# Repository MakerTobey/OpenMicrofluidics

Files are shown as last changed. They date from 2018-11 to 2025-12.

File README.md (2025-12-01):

# Note: This repository is no longer expanded, instead, several concrete development projects have come out of it, including
* [A modular strobe workstation for microfluidic droplet generation](https://wenzel-lab.github.io/strobe-enhanced-microscopy-stage/)
* [A modular microfluidics flow controller](https://github.com/wenzel-lab/modular-microfluidics-workstation-controller)
* [RITMOS: Real-tIme Technology for Microfluidic drOplet Sorting](https://github.com/wenzel-lab/droplet-sorter-master/blob/main/README.md)
* [Syringe pumps optimised for microfluidics](https://github.com/wenzel-lab/syringe-pumps-and-controller)
* and more
* PLEASE SEE THE [REPOSITORIES OF OUR RESEARCH LABORATORY](https://github.com/orgs/wenzel-lab/repositories)

# Free and Open Source Microfluidics Research Hardware

This GitHub repository is an in-progress collection of Open Source Hardware instrumentation for microfluidics and ultra-high troughput lifescience experimentation research. This is a community driven effort and **you are invited to contribute thoughts, content, comments and help testing the instrumentation**! 

This projekt started as part of my Fellowship Freies Wissen (translates to Open Knowledge)2018-2019, here is the [project description on the corresponding Wikiversity page](https://de.wikiversity.org/wiki/Wikiversity:Fellow-Programm_Freies_Wissen/Einreichungen/Open_labware_for_better_life_science). And is beeing further developed as part of my reseach efforts as well as in my free time, togehter with various project partners, such advice and help from Daniel Mietchen, Patrick Hasenfeld, Nicolas Peschke, Biotop Community Heidelberg, the EMBL Workshops (especially Christian Arnold and Alejandro Gil Ortiz), and others.

## The following aim is addressed in this repository:

This is a list of microfluidics relevant Open Source Harwdare instrumentation, connected to the practical aim of testing the documentations by reading them carefully, by building the instrumentation in some cases (remotely and Heidelberg based workshop in early 2019) and further by testing, comparing and calibrating the equipement. **Everyone is welcome to contribute**.  Please contact me directly (Tobias.Wenzel /at/ embl.de) if you need financial help with hardware parts in oder to test the documentations and redocument them on [DocuBricks](docurbricks.com) to create more accessible, open hardware standard documentations.

### Happy contributing!

# Openess of microfluidics research & developement and ways forward

Increasing openess can be acheived in many different ways, such as increased accessibility of techniques or results to a professional or general audience, greater ease of use, increased mobility of researchers of different seniority, discipines or ethnicity into the field.
One aspect that enjoys recent popularity in microfluidic and bioprocess technologies is the "biohacker"or Do-It-Yourself (DIY) biology movement. The later includes self-made and low-cost research instrumentation.
Such advances in openess greatly improve the accessibility of microfluidic and related technology to lay people and have been reviewed recently [akerspaces." Trends in Biotechnology (February 3, 2017). https://doi.org/10.1016/j.tibtech.2017.01.001].
The open source hardware originating from this context does usually not, however, fulfill key application relevant criteria such as basic safety mechanisms (e.g. dremel fuge), bencharking calibration assessment (e.g. XXX), and documentation best practices as reccomended by the GOSH community [e.g. https://www.docubricks.com/best-practise-guide.jsp] or the Journal of Open Hardware, OSWA, etc.
For the above reasond of focus and qality management, here we focus on hardware and manufacturing related aspects of microfluidic and related technology for professional (in particular academic) applications.
In particular we probe 

(I) the use of open platforms and software.

(II) digitalisation and use/challenges of digital manufacturing

(III) identification of potentially valualble resources for microfluidic research drawing on digital manufacturing, open source and publis resources.
* high quality small-scale fluidic chip manufacturing techniques
* imaging of droplets (normal, fhigh-speed (e.g. stroboscopic+software), fluorescence)
* sorting of droplets (hardware-fast-processing, software, instructions)
* pressure control
* simlation tools
* open reagents 

# Free and Open Source Hardware resources of interest for testing and further development - selected promising resources

Any contribution and participation welcome! I am happy to connect and perhaps even help with resources, parts and potential parts-funding! Comment here, via issues, or email me.

## Open Dropseq station and Open Digital PCR

After looking at the details of the project, this seems like a fantastic piece of hardware and documentation. We will definitely try to build it and have already ordered all parts. Nice small and low-cost solutions for pressure controll. Parts are being purchased at the moment. Please look into the respective sub-repository: 

https://github.com/MakerTobey/OpenMicrofluidics/tree/master/Minidrop%20build%20and%20test

https://metafluidics.org/devices/minidrops/
https://www.nature.com/articles/s41467-017-02659-x#Sec9

### Open Fluorescence Activated Droplet Sorting

This is an active contsturction project! For files and progress, please look into the respective folder in this repository: https://github.com/MakerTobey/OpenMicrofluidics/tree/master/Open%20Fluorescence%20Activated%20Droplet%20Sorting%20(FADS)

FACS (Fluorescence Activated Cell Sorting) equivalent sorting of droplets for directed evolution and many other essays is a key method in microfluidics that only few labs master. One of the reasons is that few instructions are available (but they do exsist! See Christoph Merten in Nature Methods), and equipemnt is complex, propriatory and very expensive. A common work station for droplet sorting usually costs ca. 100.000 Euro. Now, an open source version (no propriatory sorware and harware lock-in, modifiable, modular and extensible) comes within reach!

## Open microfluidics pressure control

### Open syringepump(s)

http://www.appropedia.org/Open-source_syringe_pump
We have built two, but will further upgrade and test.

http://www.appropedia.org/Lynch_open_source_syringe_pump_modifications
https://www.sciencedirect.com/science/article/pii/S2468067218300269

We are building and testing some of this hardware! Please look into the respective project subfolder: https://github.com/MakerTobey/OpenMicrofluidics/tree/master/pressure%20control%20build%20and%20test

### Open pressure controll

My own project to build an ardunino based 2-channel pressure controll (pressure derived from a compressor), to be extended and tested: https://www.docubricks.com/viewer.jsp?id=6067044959053384704 Also explore our seperate GitHub repository: https://github.com/MakerTobey/uFluid

This project looks similar and deserves further attention: https://hackaday.io/project/148274-electronic-pressure-regulator, https://github.com/watsaig/ufcs-pc

A useful manifold for quake-style valves, already build and soon to be tested: https://github.com/GNHua/valve-control

Another useful manifold for quake-style valves, to be tested soon: https://metafluidics.org/devices/32-channel-controller/ Is this documentation incomplete?

In this project and with colleagues, we are following up on thiese hardware pieces. The Minidrop station includes another curstom pressure controll implementation.

## Open digital microfluidics ... and other related

OpenDrop
http://www.gaudi.ch/GaudiLabs/?page_id=392

And Dropbot
http://microfluidics.utoronto.ca/dropbot/

## Open digital microscopy

Open Flexure Microscope
https://aip.scitation.org/doi/10.1063/1.4941068
https://www.docubricks.com/viewer.jsp?id=6067044959053384704
with objective:
https://github.com/rwb27/openflexure_microscope
with motorisation:
https://github.com/rwb27/openflexure_nano_motor_controller
We are currently waiting for the new release (large, with automation and objective) to build one.

FlyPi:
https://open-labware.net/projects/flypi/
https://journals.plos.org/plosbiology/article?id=10.1371/journal.pbio.2002702

## Open fast-imaging solutions

Note: in the meanwhile, a sulution has been published: https://www.hardware-x.com/article/S2468-0672(22)00112-2/fulltext. We have also implemented and tested our own modular-but-integrated solution which can be found in our open microfluidics workstation repository: https://github.com/wenzel-lab/open-microfluidics-workstation

No microfluidics related fast imaging open hardware projects are konwn to us so far! Please let me know if you are aware of a resource. Fast-responding cameras would be great or stroboscopic illumination for droplet microfluidics.

I believe that stroboscopic imaging has already been build by many labs. Who would be interested to publish the designs openly?

Paper references of possible interest:
https://www.hindawi.com/journals/jamc/2009/198732/
https://aapt.scitation.org/doi/abs/10.1119/1.4863916
https://www.mdpi.com/2072-666X/8/12/351
https://www.future-science.com/doi/abs/10.2144/000112220
https://www.sciencedirect.com/science/article/pii/S0165027012003846
This link is broken at the moment! What content was here?  -> https://media.proquest.com/media/pq/classic/doc/4322030507/fmt/ai/rep/NPDF?_s=EUAbzVz%2B%2FEKGyiix9oguFSmtgAU%3D

Maybe:
https://pdfs.semanticscholar.org/63f0/b73d48380f3d5d3614e0fe12ae55adaeb1dd.pdf
https://www.spiedigitallibrary.org/conference-proceedings-of-spie/5145/0000/Simultaneous-mapping-of-phase-and-amplitude-of-MEMS-vibrations-by/10.1117/12.500138.short?SSO=1
https://scholar.google.de/scholar?hl=en&as_sdt=0%2C5&as_vis=1&q=stroboscopic%2Billumination%2Bmicroscope%2Barduino&btnG=
https://journals.plos.org/plosone/article?id=10.1371/journal.pone.0143547
https://pubs.acs.org/doi/abs/10.1021/ja074704l

Open Source imaging chips:
https://wiki.apertus.org/index.php/Main_Page

Open Source imaging software:
https://www.osapublishing.org/boe/abstract.cfm?uri=boe-1-2-385

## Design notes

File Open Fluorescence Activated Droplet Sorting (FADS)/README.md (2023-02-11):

# Open Fluorescence Activated Droplet Sorting (Open FADS)

FACS (Fluorescence Activated Cell Sorting) equivalent sorting of droplets for directed evolution and many other essays is a key method in microfluidics that only few labs master. One of the reasons is that few instructions are available (but they do exsist! See Christoph Merten in Nature Methods), and equipemnt is complex, propriatory and very expensive. A common work station for droplet sorting usually costs ca. 100.000 Euro. Now, an open source version (no propriatory sorware and harware lock-in, modifiable, modular and extensible) comes within reach! 

The current focus of this project is the FPGA data processing, which is worked on in this repository: https://github.com/MakerTobey/Open_FADS_FPGA_control
We are now also finalising the optomechanics part of the project here: [https://github.com/WenzelLab/Open_FADS_optomechanics](https://github.com/wenzel-lab/Open_FADS_optomechanics)

# These are the things needed for a FADS workstation:

## light source
This requires a strong lightsource (laser, most commonly 488nm {for Green Fluorescent Protein (GFP), red RFP and similar}, collimated, small elliptical focal spot, low coherence to avoid speckles) to activate fluorescence. Lasers usually cost several thousand Euro but some cheaper ones are available at slightly different wavelengths https://www.dragonlasers.com/blue-laser-pointers.html. Usually one has to calculate with a few thousand Euro per laser and some additional hundred Euro for the optics (not counting a professional microscope). Here we explore how to keep costs reasonably low while maintaining the quality and specifications of the setup.

## fast and sensitive fluorescence detection
It requires a fast and very sensitive detector for the fluorescent signal. This is commonly a PMT (photomultiplier tube), but now there are cheaper and less-easy-to-break APDs (avalanche photodiode)s. Individually they should cost in the order of magnitude of a hundred Euro, but they need to be hosted on a controller, cooling, etc. unit with appropriate connector, which usually spikes the cost to thousands. However, now there is work on an open source APD controller:
OpenAPD:

http://www.gaudi.ch/GaudiLabs/?page_id=718

Some circuits (e.g. amplification) might be useful from the CosmicPi projekt:

https://github.com/CosmicPi/CosmicPiV1.6PCB

https://ieeexplore.ieee.org/document/5158737

Here we use a non-open source, but lower noise, more modern, silicon based (does not break as easily) SiPM module from Ketek in Germany.

## fast data processing
And then there is a need for a very fast real-time logical processor chip, which is usually achieved by programming an FPGA chip. This chip will read the signal and make a decision whether or not to activate the droplet sorter. (For example: Positive signal is coming in, intensity and duration (width) is in the right range and there was no other signal too shortly before, so OK, activate the amplifier trigger for the sorting electrode.) FPGAs are usually not exacly user friendly as they are programmed in a bottom-level hardware language. Easy-to-use systems (with integrated top level languages for programming and common measurement-tech interfaces) usually some in a propriatory environment and are very expensive. However, there has been a lot of activity in the respective open source landscape recently.

Medium cost, established for science measurements:

Red Pitaya https://www.redpitaya.com This has been now purchased for testing from Reichelt Electronik (reichelt.de, January 2019):

Part Nr | Description | Price
--- | --- | ---
STEMLAB 14 UK | we bought this complete kit: USB-Messlabor STEMlab 125-14 Ultimate Kit, 2 Kanäle, 50 MHz, USB | 624,00 EUR 
STEMLAB 14 SK | But this unit would have been sufficient: USB-Messlabor STEMlab 125-14 Starter Kit, 2 Kanäle, 50 MHz, USB | 308.00 EUR
shipping | shipping | 5.60 EUR

Newer projects to make FPGAs accessible, still require advanced electronics or programming knowledge:

http://www.clifford.at/icestorm/ https://media.ccc.de/v/32c3-7139-a_free_and_open_source_verilog-to-bitstream_flow_for_ice40_fpgas

https://hackaday.com/2018/12/13/icebreaker-the-open-source-development-board-for-fpgas/

http://papilio.cc (more light weight)

The processing is currently beeing worked on using the Red Pitaya as a platform. This work is hosted in this seperate repository https://github.com/MakerTobey/Open_FADS_FPGA_control

## high voltage AC pulse generation for dielectrophoretic droplet movement

Here is an estimate of the specs that are beeing used for high-end droplet sorting:

A voltage of ca. 0.1-3kV (at quasi zero Ampere current) is applied to the electrodes on chip. This depends quite a lot on the electrode geometry and the forces required. Using longer electrodes (Rails etc.) Sub 1kV voltages are sufficient (see "Rational design of a high-throughput droplet sorter" Lab on a Chip 2019, DOI: 10.1039/c9lc00149b https://pubs.rsc.org/en/content/articlelanding/2019/LC/C9LC00149B#!divAbstract)

0.4-3 milisecond (ms) pulses sent to the electrodes on chip (depending on droplet size, speed and electrode shape). This needs to happen with usually no more than a 100us delay after detecting the fluorescent signal, as the drops move fast.

The pulse itself is then still alternating current (AC), with a frequency of ca. 0.1-80kHz frequency (generalisation: the higher the frequency in these limits, the stronger is the force on the droplet). Starting value for our project: 20kHz or higher. *Question: How can this value be smaller or equal the droplet sorting rate?*

Apparently [square wave (DC-DC) pulses are more efficient for dielectrophoresis than AC waves](https://www.google.com/url?sa=t&rct=j&q=&esrc=s&source=web&cd=2&cad=rja&uact=8&ved=2ahUKEwiIjt2c94HhAhWHZ1AKHfeSCYYQFjABegQIABAC&url=https%3A%2F%2Ftigerprints.clemson.edu%2Fcgi%2Fviewcontent.cgi%3Farticle%3D1016%26context%3Dmecheng_pubs&usg=AOvVaw1J-VG6QFMguafNriVgkh64). This is also what most people in the field (who mention it) seem to use if they can. Generating these signals is not so hard - there are many decent small, open and cheap function generators. This can also easily be done on the same FPGA computer that is already used for data processing.

However, amplification of these pulses is hard and there seem to be only two equipment providers (Trek and Matsusada). The amplifiers are expensive (ca. 5-10 kEuro), large, heavy and energy consuming.

However, since we only need a square wafe signal with stable levels, there seems to be an opportunity to build a switch chip using with voltage power converter units (e.g. APS models from ISEG https://iseg-hv.com/en/products/dc-dc) and voltage tollerant MOSFETs (e.g. https://de.rs-online.com/web/p/mosfet/8016794/).

Recently (Summer 2020) a paper was published (https://advances.sciencemag.org/content/6/22/eaba6712) containing a "booster" design to amplify microfluidic sorting pulses to 2kV at 80kHz (but sine wave only). 
A variant of this design was tested and was successfully able to sort 50um droplets (using 50kHz frequenzy - square input, output half-square-half-sine, and ca. 1.3kV). This is a great compact and low-cost alternative to the big electrophoresis amplifyers commonly used for this purpose in the literature.

## MRS thread for objective coupling

https://cad.onshape.com/documents/e13576e52de2a4dca37d5abe/w/be82327607e232eebe074e90/e/e5f94c1374d0ac1eb65df4f6?renderMode=0&uiState=63e15775e1f68c2311f80855

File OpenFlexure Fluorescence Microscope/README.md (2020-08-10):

# OpenFlexture Fluorescence Microscope
## This build is a fork of the Open Flexture Microscope version 6.0
A transmission + epi-fluorescence microscope version has successfully been build based on it.

This is a fork of the [OpenFlexure Microscope](https://github.com/rwb27/openflexure_microscope) release [beta 6.0](https://gitlab.com/openflexure/openflexure-microscope/-/releases).

STL files are available at build.openflexure.org/openflexure-microscope/v6.0.0/
Documentation is available at build.openflexure.org/openflexure-microscope/v6.0.0/docs

And the files (for V6.1.1. with minor further improvements) is available in a subfolder of this repository, including extra files needed for the epi-fluorescence assembly.

In this repository, the design is beeing modified for fluorescence application.
The official [discussion on a fluorescence version of the OpenFlexure Microscope takes place here](https://gitter.im/OpenFlexureProject/Fluorescence?source=orgpage).

## Fluorescence illumination with bright star-LED

For strong fluorescnece stimulation, we use a high-power LED solution, based the illumination used here: https://pubs.acs.org/doi/10.1021/acs.analchem.7b04689

We purchased the folloing from Luxeonstar.com (February 2019):

Part Nr | Description | Price
--- | --- | ---
SP-01-B6 | LED: Blue (470nm) Rebel LED (LXML-PB02) on a SinkPAD-II 20mm Star Base - 74lm @ 700mA  | 13.08 $US
10193 | Carclo 8.7° 20 mm Circular Beam Optic - No Holder | 2.60 $US
10235 | Carclo 20 mm Black Round Optic Holder - Flat Bottom | 0.70 $US
LXT-S-12 | Pre-Cut, Thermal Adhesive Tape for 20 mm Star LED Assemblies - (12 Piece Sheet)| 7.49 $US
N30-10B | 30 mm Square x 10 mm High Alpha Heat Sink - 14.0 °C/W 10193 Carclo 8.7° 20 mm Circular Beam Optic - No Holder | 5.72 $US
LP-01 | Assembly Press for Mounting Single Rebel LED Assemblies to a Heatsink | 0.00 $US
shipping | Shipping to Europe | 21.01 $USD

## optical filters

The filters from [Comar Optics (UK)](https://www.comaroptics.com/components/filters) seem to have a good price range. I ordered the following filters to integrate into the [Open Flexturescope](https://github.com/rwb27/openflexure_microscope/issues/43). I ordered the parts in March 2019 and more January 2020.

Part Nr | Description | Price in GBP
--- | --- | ---
495 IK 116 | (Excitation filter, Shortpass 495) Dichroic filter, 25 x 16 x 1.1mm | £21.34
550 IY 125 | (Dichroic beam splitter, Longpass 506) Dichroic filter, 50 x 50 x 1.1mm | £47.19
510 IY 50 | (Emission filter, Longpass 519) Dichroic filter, 50 x 50 x 1.1mm | £47.19
--- | --- | ---
525 IB 25 | Dichroic filter, band pass, 500/550nm, dia 25mm x 1mm | £26.07
585 AY 25 | Acrylic colour filter, 585nm longpass, 25mm diameter x 1mm | £9.24
635 IY 125 | Dichroic filter, long pass, 635nm, 40 x 25 x 1.1mm | £38.24
40 BA 00 | Plate beamsplitter, standard, visible 50%, 40mm diameter x 3mm(thick!) | £37.07

Shipping with Comar Priority Service to Germany - £24.65

The first three filters form a GFP, Fluorescine etc. standard fluorescence set. The later filters can extend the stack to Propidium Iodite (PI) filtering in the yellow fraction of the spectrum.

Jointly with the Biotop community in Heidelberg, we made a first fluorescence microscope version with a blue star LED.

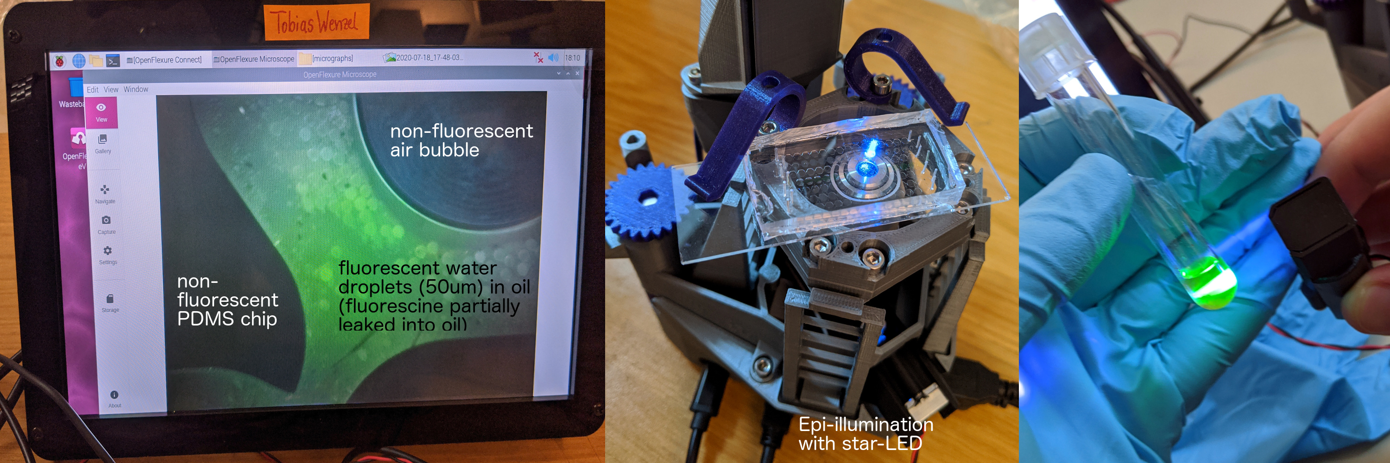
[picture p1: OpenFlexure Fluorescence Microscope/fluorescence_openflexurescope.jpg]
 

I used the SunFounder 10.1 Inch Raspberry Pi High-Res Monitor (119,99 € on Amazon.de) and a Rapberri Pi V4 (4GB RAM) to run the microscope and look at the images.

## Related aspects to this projects are beeing discussed on the [Open FADS part of this repository](https://github.com/MakerTobey/OpenMicrofluidics/tree/master/Open%20Fluorescence%20Activated%20Droplet%20Sorting%20(FADS)).

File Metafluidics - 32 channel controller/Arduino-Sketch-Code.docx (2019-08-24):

Supplementary Information: Arduino Sketch Code

// include the library code:

#include <LiquidCrystal.h>

// initialize the library with the numbers of the interface pins

LiquidCrystal lcd(12, 11, 5, 4, 3, 2);

// Microfluidic Ring Mixer Program (Gateway Assembly - Button Push for Final Recovery)

// Variable Declaration

const int buttonPin = 6;

int buttonState = 0;

int currentState = 0;

int beenPushed = 0;

int sensorPin = 0; //the analog pin that the TMP36's Vout (sense) pin is connected to

//the resolution is 10 mV / degree centigrade with a

//500 mV offset to allow for negative temperatures

// Setup Function

void setup()

{

// set up the LCD's number of columns and rows:

lcd.begin(16, 2);

pinMode(buttonPin, INPUT);

// valve bank 1 pin designation

pinMode(17, OUTPUT);

pinMode(18, OUTPUT);

pinMode(19, OUTPUT);

pinMode(20, OUTPUT);

pinMode(21, OUTPUT);

pinMode(22, OUTPUT);

pinMode(23, OUTPUT);

pinMode(24, OUTPUT);

//valve bank 2 pin designation

pinMode(25, OUTPUT);

pinMode(26, OUTPUT);

pinMode(27, OUTPUT);

pinMode(28, OUTPUT);

pinMode(29, OUTPUT);

pinMode(30, OUTPUT);

pinMode(31, OUTPUT);

pinMode(32, OUTPUT);

//valve bank 3 pin designation

pinMode(33, OUTPUT);

pinMode(34, OUTPUT);

pinMode(35, OUTPUT);

pinMode(36, OUTPUT);

pinMode(37, OUTPUT);

pinMode(38, OUTPUT);

pinMode(39, OUTPUT);

pinMode(40, OUTPUT);

//valve bank 4 pin designation

pinMode(41, OUTPUT);

pinMode(42, OUTPUT);

pinMode(43, OUTPUT);

pinMode(44, OUTPUT);

pinMode(45, OUTPUT);

pinMode(46, OUTPUT);

pinMode(47, OUTPUT);

pinMode(48, OUTPUT);

// initButton = digitalRead(buttonPin);

}

// Loop Continuously

void loop() {

// Get the State of the button (HIGH when not pushed, LOW when pushed)

buttonState = digitalRead(buttonPin);

// Button is pushed down, set the variable

if (buttonState == LOW) {

beenPushed = 1;

}

// When the current state is 0, set to default configuration

if (currentState == 0) {

lcd.setCursor(0, 0);

// Print a message to the LCD.

lcd.print("Genetic Circuit Assembly READY");

Ready();

tempSensor();

}

// If the button has been pushed, and is now released, execute code

if (buttonState == HIGH && beenPushed == 1) {

// Reset the push variable

beenPushed = 0;

// Increment the state

currentState = currentState + 1;

// Go do the first routine...

if (currentState == 1) {

lcd.clear();

lcd.setCursor(0, 0);

// Print a message to the LCD.

lcd.print("Latch Device1"); //Prime bank1 valves

Incubate1();

}

// Go do the first routine...

if (currentState == 2) {

lcd.clear();

lcd.setCursor(0, 0);

// Print a message to the LCD.

lcd.print("Latch Device2"); //Prime bank2 valves

Incubate2();

}

// Go do the next routine...

if (currentState == 3) {

lcd.clear();

lcd.setCursor(0, 0);

// Print a message to the LCD.

lcd.print("Block Bank 1"); //Introduce passivating agent Device1

Flow1();

}

// Go do the next routine...

if (currentState == 4) {

lcd.clear();

lcd.setCursor(0, 0);

// Print a message to the LCD.

lcd.print("Incubate Device1"); //Incubate passivating agent Device1

Incubate1();

}

// Go do the next routine...

if (currentState == 5) {

lcd.clear();

lcd.setCursor(0, 0);

// Print a message to the LCD.

lcd.print("Block Bank 2"); //Introduce passivating agent Device2

Flow2();

}

// Go do the next routine...

if (currentState == 6) {

lcd.clear();

lcd.setCursor(0, 0);

// Print a message to the LCD.

lcd.print("Incubate Device 2"); //Incubate passivating agent Device2

Incubate2();

}

// Go do the next routine...

if (currentState == 7) {

lcd.clear();

lcd.setCursor(0, 0);

// Print a message to the LCD.

lcd.print("Purge Device1"); //Flush Device1

Flow1();

}

// Go do the next routine...

if (currentState == 8) {

lcd.clear();

lcd.setCursor(0, 0);

// Print a message to the LCD.

lcd.print("Latch Bank 1");

Incubate1();

}

// Go do the next routine...

if (currentState == 9) {

lcd.clear();

lcd.setCursor(0, 0);

// Print a message to the LCD.

lcd.print("Purge Device2");

Flow2(); //Flush Device2

}

// Go do the next routine...

if (currentState == 10) {

lcd.clear();

lcd.setCursor(0, 0);

// Print a message to the LCD.

lcd.print("Latch Bank 2");

Incubate2();

}

// Go do the next routine...

if (currentState == 11) {

lcd.clear();

lcd.setCursor(0, 0);

// Print a message to the LCD.

lcd.print("Fill Device1");

Fill1();

}

// Go do the next routine...

if (currentState == 12) {

lcd.clear();

lcd.setCursor(0, 0);

// Print a message to the LCD.

lcd.print("Fill Device2");

Fill2();

}

// Go do the next routine...

if (currentState == 13) {

lcd.clear();

lcd.setCursor(0, 0);

// Print a message to the LCD.

lcd.print("Runready Device1");

Runready1();

}

// Go do the next routine...

if (currentState == 14) {

lcd.clear();

lcd.setCursor(0, 0);

// Print a message to the LCD.

lcd.print("Runready Device2");

Runready2();

}

// Go do the next routine...

if (currentState == 15) {

lcd.clear();

lcd.setCursor(0, 0);

// Print a message to the LCD.

lcd.print("Mixing Device1");

Incubate1();

for (int x = 0; x<1000; x++){

Mix1();

}

Incubate1();

}

// Go do the next routine...

if (currentState == 16) {

lcd.clear();

lcd.setCursor(0, 0);

// Print a message to the LCD.

lcd.print("Mixing Device2");

Incubate2();

for (int x = 0; x<1000; x++){

Mix2();

}

Incubate2();

}

// Go do the next routine...

if (currentState == 17) {

lcd.clear();

lcd.setCursor(0, 0);

// Print a message to the LCD.

lcd.print("Incubate Device1");

Incubate1();

}

// Go do the next routine...

if (currentState == 18) {

lcd.clear();

lcd.setCursor(0, 0);

// Print a message to the LCD.

lcd.print("Incubate Device2");

Incubate2();

}

// Go do the next routine...

if (currentState == 19) {

lcd.clear();

lcd.setCursor(0, 0);

// Print a message to the LCD.

lcd.print("Recover Device1 10s");

Flow1();

Incubate1();

}

// Go do the next routine...

if (currentState == 20) {

lcd.clear();

lcd.setCursor(0, 0);

// Print a message to the LCD.

lcd.print("Recover Device2 10s");

Flow2();

Incubate2();

}

}

}

void Ready()

{

// all microfluidic valves open

// valve bank 1

digitalWrite(17, LOW);

digitalWrite(18, LOW);

digitalWrite(19, LOW);

digitalWrite(20, LOW);

digitalWrite(21, LOW);

digitalWrite(22, LOW);

digitalWrite(23, LOW);

digitalWrite(24, LOW);

// valve bank 2

digitalWrite(25, LOW);

digitalWrite(26, LOW);

digitalWrite(27, LOW);

digitalWrite(28, LOW);

digitalWrite(29, LOW);

digitalWrite(30, LOW);

digitalWrite(31, LOW);

digitalWrite(32, LOW);

// valve bank 3

digitalWrite(33, LOW);

digitalWrite(34, LOW);

digitalWrite(35, LOW);

digitalWrite(36, LOW);

digitalWrite(37, LOW);

digitalWrite(38, LOW);

digitalWrite(39, LOW);

digitalWrite(40, LOW);

// valve bank 4

digitalWrite(41, LOW);

digitalWrite(42, LOW);

digitalWrite(43, LOW);

digitalWrite(44, LOW);

digitalWrite(45, LOW);

digitalWrite(46, LOW);

digitalWrite(47, LOW);

digitalWrite(48, LOW);

}

void Incubate1()

{

// Latch valves for bank 1

digitalWrite(17, HIGH);

digitalWrite(18, HIGH);

digitalWrite(19, HIGH);

digitalWrite(20, HIGH);

digitalWrite(21, HIGH);

digitalWrite(22, HIGH);

digitalWrite(23, HIGH);

digitalWrite(24, HIGH);

}

void Incubate2()

{

// Latch valves for bank 2

digitalWrite(25, HIGH);

digitalWrite(26, HIGH);

digitalWrite(27, HIGH);

digitalWrite(28, HIGH);

digitalWrite(29, HIGH);

digitalWrite(30, HIGH);

digitalWrite(31, HIGH);

digitalWrite(32, HIGH);

}

void Flow1()

{

digitalWrite(17, HIGH);

digitalWrite(18, LOW);

digitalWrite(19, LOW);

digitalWrite(20, LOW);

digitalWrite(21, LOW);

digitalWrite(22, LOW);

digitalWrite(23, HIGH);

digitalWrite(24, LOW);

}

void Flow2()

{

digitalWrite(25, HIGH);

digitalWrite(26, LOW);

digitalWrite(27, LOW);

digitalWrite(28, LOW);

digitalWrite(29, LOW);

digitalWrite(30, LOW);

digitalWrite(31, HIGH);

digitalWrite(32, LOW);

}

void Fill1()

{

// Purge ring with air

digitalWrite(17, LOW);

digitalWrite(18, HIGH);

digitalWrite(19, LOW);

digitalWrite(20, LOW);

digitalWrite(21, LOW);

digitalWrite(22, HIGH);

digitalWrite(23, LOW);

digitalWrite(24, HIGH);

}

void Fill2()

{

// Purge ring with air

digitalWrite(25, LOW);

digitalWrite(26, HIGH);

digitalWrite(27, LOW);

digitalWrite(28, LOW);

digitalWrite(29, LOW);

digitalWrite(30, HIGH);

digitalWrite(31, LOW);

digitalWrite(32, HIGH);

}

void Runready1()

{

// green LED to signal block done and OK to run protocol

digitalWrite(17, HIGH);

digitalWrite(18, HIGH);

digitalWrite(19, LOW);

digitalWrite(20, LOW);

digitalWrite(21, HIGH);

digitalWrite(22, HIGH);

digitalWrite(23, HIGH);

digitalWrite(24, HIGH);

}

void Runready2()

{

// green LED to signal block done and OK to run protocol

digitalWrite(25, HIGH);

digitalWrite(26, HIGH);

digitalWrite(27, LOW);

digitalWrite(28, LOW);

digitalWrite(29, HIGH);

digitalWrite(30, HIGH);

digitalWrite(31, HIGH);

digitalWrite(32, HIGH);

}

void Mix1()

{

// peristaltic pump routine (25 Hz)

digitalWrite(17, HIGH);

digitalWrite(18, HIGH);

digitalWrite(22, LOW);

digitalWrite(23, HIGH);

digitalWrite(24, HIGH);

digitalWrite(19, LOW);

digitalWrite(20, LOW);

digitalWrite(21, LOW);

delay(40);

digitalWrite(19, HIGH);

digitalWrite(20, LOW);

digitalWrite(21, LOW);

delay(40);

digitalWrite(19, HIGH);

digitalWrite(20, HIGH);

digitalWrite(21, LOW);

delay(40);

digitalWrite(19, HIGH);

digitalWrite(20, HIGH);

digitalWrite(21, HIGH);

delay(40);

digitalWrite(19, LOW);

digitalWrite(20, HIGH);

digitalWrite(21, HIGH);

delay(40);

digitalWrite(19, LOW);

digitalWrite(20, LOW);

digitalWrite(21, HIGH);

delay(40);

}

void Mix2()

{

// peristaltic pump routine (25 Hz)

digitalWrite(25, HIGH);

digitalWrite(26, HIGH);

digitalWrite(30, LOW);

digitalWrite(31, HIGH);

digitalWrite(32, HIGH);

digitalWrite(27, LOW);

digitalWrite(28, LOW);

digitalWrite(29, LOW);

delay(40);

digitalWrite(19, HIGH);

digitalWrite(20, LOW);

digitalWrite(21, LOW);

delay(40);

digitalWrite(27, HIGH);

digitalWrite(28, HIGH);

digitalWrite(29, LOW);

delay(40);

digitalWrite(27, HIGH);

digitalWrite(28, HIGH);

digitalWrite(29, HIGH);

delay(40);

digitalWrite(27, LOW);

digitalWrite(28, HIGH);

digitalWrite(29, HIGH);

delay(40);

digitalWrite(27, LOW);

digitalWrite(28, LOW);

digitalWrite(29, HIGH);

delay(40);

}

void Incubate1()

{

// Latch valves for bank 1

digitalWrite(17, HIGH);

digitalWrite(18, HIGH);

digitalWrite(19, HIGH);

digitalWrite(20, HIGH);

digitalWrite(21, HIGH);

digitalWrite(22, HIGH);

digitalWrite(23, HIGH);

digitalWrite(24, HIGH);

}

void Incubate2()

{

// Latch valves for bank 1

digitalWrite(25, HIGH);

digitalWrite(26, HIGH);

digitalWrite(27, HIGH);

digitalWrite(28, HIGH);

digitalWrite(29, HIGH);

digitalWrite(30, HIGH);

digitalWrite(31, HIGH);

digitalWrite(32, HIGH);

}

void Recover1()

{

//moves the ligated product to the chip outlet for recovery

digitalWrite(17, HIGH);

digitalWrite(18, LOW);

digitalWrite(19, LOW);

digitalWrite(20, LOW);

digitalWrite(21, LOW);

digitalWrite(22, LOW);

digitalWrite(23, HIGH);

digitalWrite(24, LOW);

delay(10000);

}

void Recover2()

{

//moves the ligated product to the chip outlet for recovery

digitalWrite(25, HIGH);

digitalWrite(26, LOW);

digitalWrite(27, LOW);

digitalWrite(28, LOW);

digitalWrite(29, LOW);

digitalWrite(30, LOW);

digitalWrite(31, HIGH);

digitalWrite(32, LOW);

delay(10000);

}

void tempSensor()

{

//getting the voltage reading from the temperature sensor

int reading = analogRead(sensorPin);

// converting that reading to voltage, for 3.3v arduino use 3.3

float voltage = reading * 5.0;

voltage /= 1024.0;

float temperatureC = (voltage - 0.5) * 100 ; //converting from 10 mv per degree wit 500 mV offset

//to degrees ((volatge - 500mV) times 100)

lcd.setCursor(12, 1);

// Print a message to the LCD.

lcd.print(temperatureC,0);

lcd.setCursor(14, 1);

lcd.print("C");

}

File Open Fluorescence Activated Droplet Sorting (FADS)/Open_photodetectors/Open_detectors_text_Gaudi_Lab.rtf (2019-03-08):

DIY Open Source Single Photon Generator and Detector
Single photons are cool. By generating and detecting single photons new experiments in physical science and quantum mechanics are possible. Great applications like quantum computing and cryptography, medical and biotechnological measurements, as well as environmental monitoring are based on single photons. So we need to build a DIY Open Source Single Photon Generator and Detector for everyone to play with. There seem to be different aproaches on how to generate single photons. By fluorescent suspended ions, quantum nano-dots or through non linear crystals (BBO crystal or KDP crystal). The later uses so called Spontaneous Parametric Down-Conversion (SPDC) and will create two entangled photons simultaneously (if the frequencies are right).
Single Photon Detectors
To detect the single photons we need open source single photon detectors. There are several ways of detecting very low light:
Photon Multiplier Tube (PMT), the classic way, a glass tube with several stages that when supplied with high voltage will multiply electrons generated by the incident photon. These tubes are available for quite cheap on internet or even full luminometers with photon multiplier tubes can be found.
Charged Coupled Device (CCD) with low noise when cooled down are the classic way to get a very low light and reproducable image. These are used in special microscopes and ofter super expensive.
Electron Multiplying CCD (EMCCD) combine the multiplying effect of the multiplier tube with the CCD sensor. And thus are even more expensive.
sCMOS – CMOS (Complementary Metal Oxide Semiconductor) chips replaced CCD in consumer and even professional photo cameras. With the sCMOS, a scientific grade of CMOS, this technology is now entering the market of scientific imaging and hopefully bringing down the prices.
Then there are two relatively inexpensive and still sensitive semiconductor devices that are interesting for photon detection:
Avalanche photodiodes (APD) are small discrete detectors that exploits the photon-triggered avalanche current of a reverse biased p-n junction to detect the photons. The higher the reverse voltage (80-200 VDC) the bigger the avalanche multiplication (acts like an internal amplification). With a relatively simple circuit providing high voltage at limited current and a high gain, low noise amplifier, these devices are very fast and sensitive photo detectors. The OpenAPD is an open source device for such a circuit.
Single Photon Avalanche Diodes (SPAD), special avalanche photo diodes, which operate above the breakdown voltage in so called Geiger mode. When a photon hits the detector an on going avalanche is triggered that turns the diode “on”. The diode is then reset “off” to be ready for the next photon. Thus these elements create a digital signal (one click per photon, thus the name of Geiger mode I guess). The set and reset of the diode can be achieved with a passive quenching (just a resistor in series). Or with an active avalanche-quenching circuits. The OpenSPAD implements such an active quenching circuits as described in scientific literature.
OpenAPD
Open source hardware design of drive, amplification and cooling circuit for Avalanche photodiodes (APD).
The design is manly based on the MAX1932, Digitally Controlled, 0.5% Accurate APD Bias Supply, a single OpAmp amplifier and a Arduino Micro to control and read the signals.
(http://www.gaudi.ch/GaudiLabs/?attachment_id=725)
Schematic of the OpenAPD
(http://www.gaudi.ch/GaudiLabs/?attachment_id=724)
Drive and Amplifier Schematic of the OpenAPD
(http://www.gaudi.ch/GaudiLabs/?attachment_id=730)
The design is still being tested and may contain errors. Please leave your comments and suggestions in the comment section.
OpenSPAD
Open source hardware design of drive, timing and cooling circuit for Single Photon Avalanche Diodes (SPAD). The design of the OpenSPAD is closely based on the schematic proposed by the paper “An Integrated Active-Quenching Circuit for Single-Photon Avalanche Diodes”, Franco Zappa (2000).
(http://www.gaudi.ch/GaudiLabs/?attachment_id=726)
Schematic of the OpenSPAD
The design is still being tested and may contain errors. Please leave your comments and suggestions in the comment section.
yGauge
A lowest luminosity reference. For more details see here (http://www.gaudi.ch/GaudiLabs/?page_id=740).
(http://www.gaudi.ch/GaudiLabs/?attachment_id=744)
References:
“Active quenching and gating circuits for single photon avalanche photodiodes (SPADs)”, S. Cova (1982)
“An Integrated Active-Quenching Circuit for Single-Photon Avalanche Diodes”, Franco Zappa (2000)
“Single Photon Counting Module Based on Large Area APD and Novel Logic Circuit for Quench and Reset Pulse Generation”, Vinit H. Dhulla, (2007)
“Free-running InGaAs/InP single photon detector with feedback quenching IC”, Fu Zheng (2015)
Avalanche-Photodioden
LaserComponents Single Phototn Detector, Cooled, Queltch
SPAD array.
electron multiplying charge coupled devices (EMCCDs)
sCMOS camera
http://www.everyphotoncounts.com/spad.php
Human eye can apparently detect single photons. (according to the article from NATURE COMMUNICATIONS: “Direct detection of a single photon by humans”)
Non Linear Crystals:
Monopotassium phosphate (KDP)
Potassium titanyl phosphate (KTP)
Beta barium borate (BBO)
KTP cristals can be found in cheap green lasers:
monolithic (multiple) crystal assembly (MCA) : ND:YVO4 – > KTP (808nm – > 1064nm – > 532nm)
Comercial non linear cristals: http://www.altechna.de
Lasers:
Lasers from DVD:
780nm CD
650nm DVD
405nm HD DVD BlueRay
neodymium-doped lasers:
Nd:YAG laser,
Nd:YLF lasers
Spontaneous Parametric Down-Conversion (SPDC):
SPDC is a quantum optical technique in which correlated pairs of photons (called signal and idler) are produced probabilistically from a higher energetic pump photon in a non-linear crystal following energy and momentum conservation.
Further Reading:
quantum information theory
quantum fluctuation vacuum fluctuation
Advanced Microscopy :
– stimulated emission depletion (STED)
– structured illumination microscopy (SIM)
– stochastic optical reconstruction microscopy (STORM),
– photoactivated localization microscopy (PALM)
– Single-molecule nanoscopy (based on switchable fluorescent molecules)
Leave a Reply
You must be logged in (http://www.gaudi.ch/GaudiLabs/wp-login.php) to post a comment.
BizzCard (http://themezee.com/)

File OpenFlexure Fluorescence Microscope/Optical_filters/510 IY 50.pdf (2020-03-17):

510 IY 50

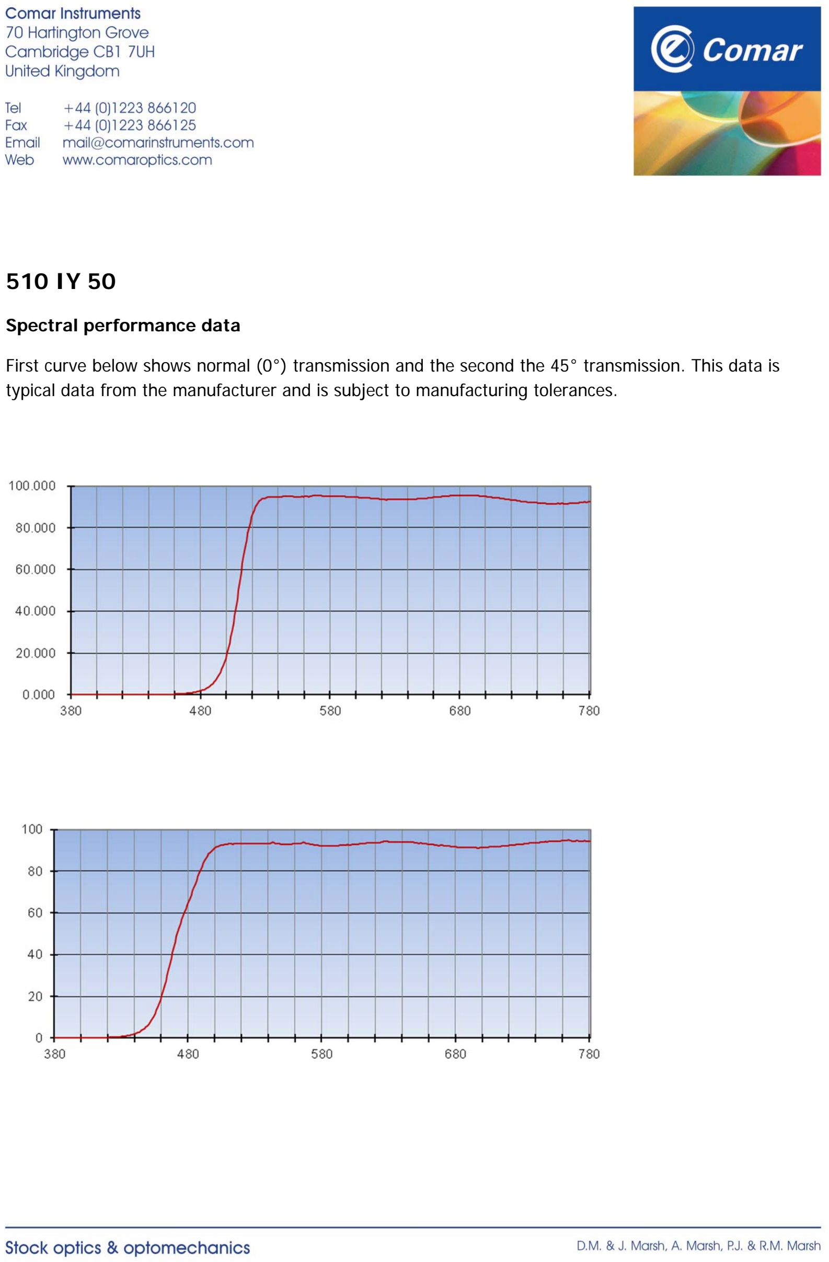
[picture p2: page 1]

Spectral performance data

First curve below shows normal (0°) transmission and the second the 45° transmission. This data is typical data from the manufacturer and is subject to manufacturing tolerances.

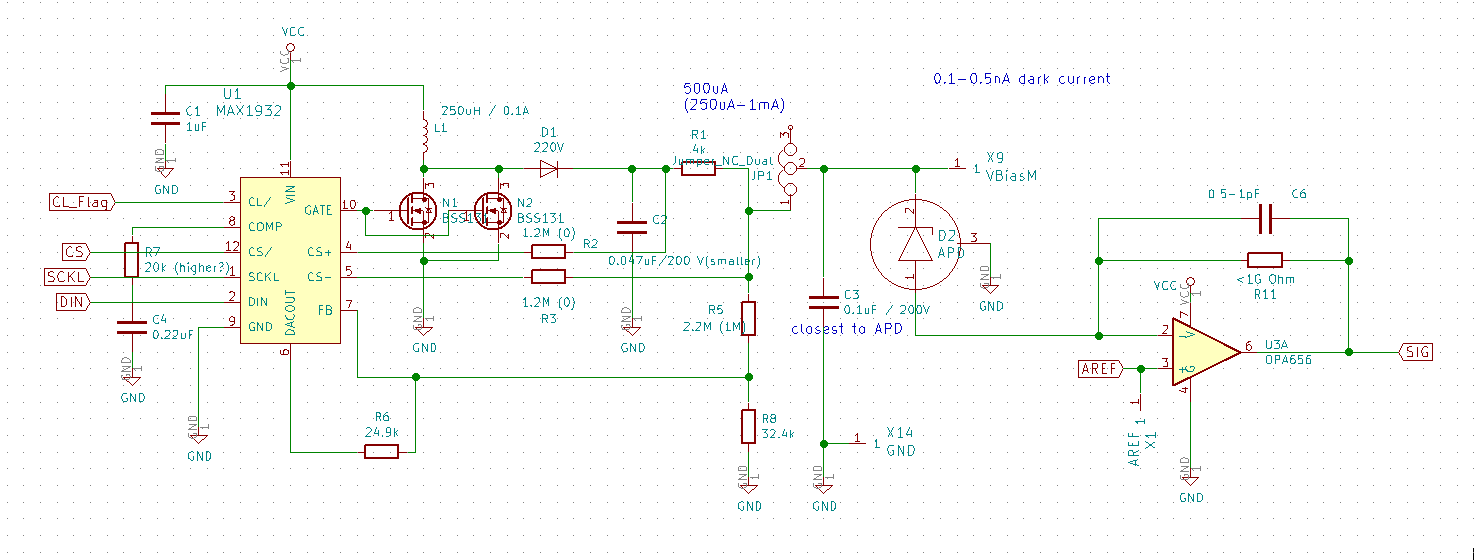
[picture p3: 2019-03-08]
Open Fluorescence Activated Droplet Sorting (FADS)/Open_photodetectors/Open_APD_with_comments_by_Klaus_Viebig/OpenAPD__Schematic-extra fine.png

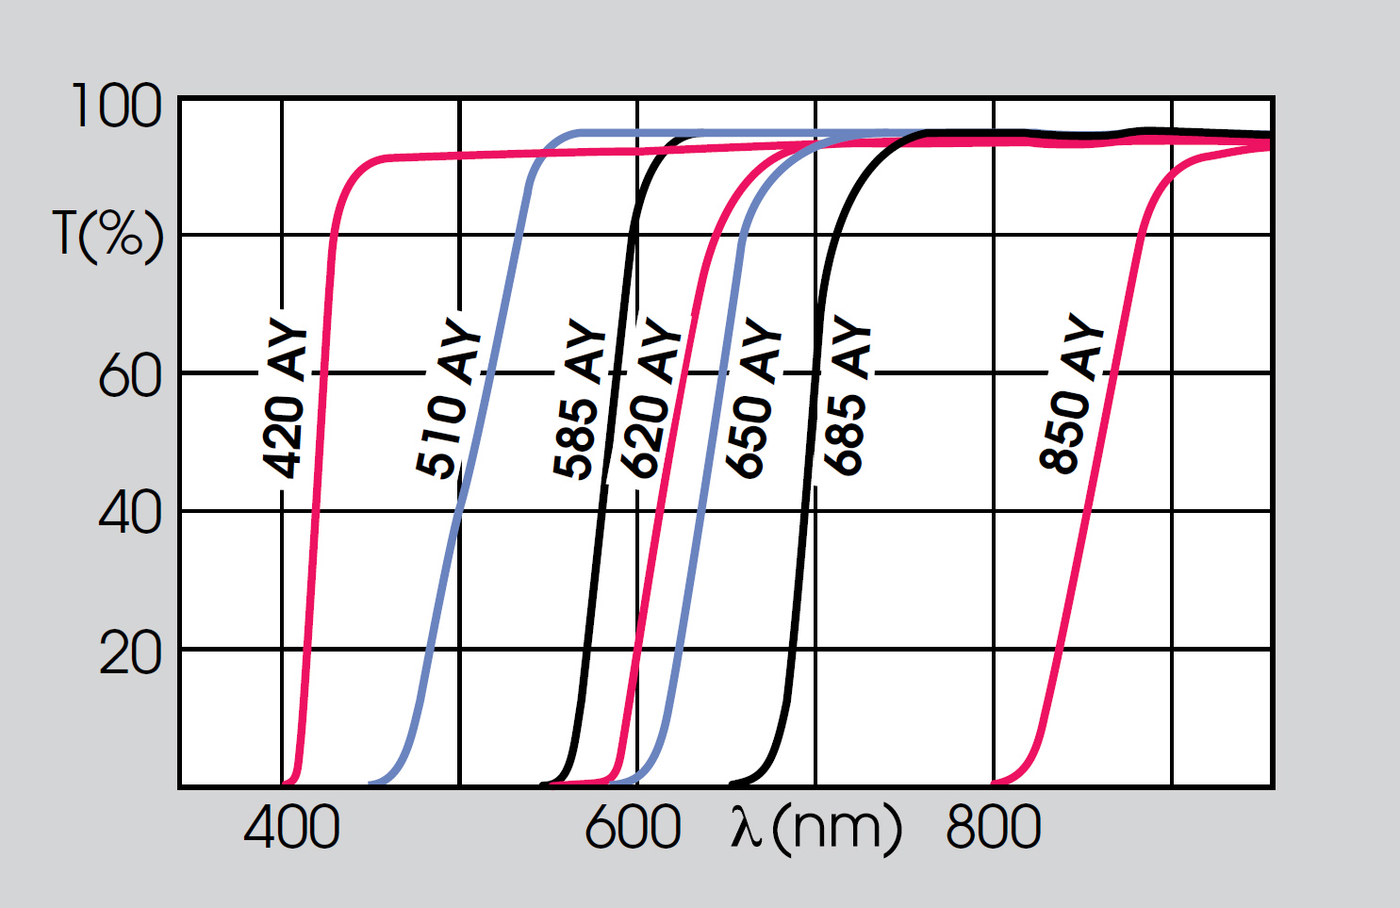
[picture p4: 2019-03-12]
OpenFlexure Fluorescence Microscope/Optical_filters/585 AY 25 acrylic filters AY curves.jpg

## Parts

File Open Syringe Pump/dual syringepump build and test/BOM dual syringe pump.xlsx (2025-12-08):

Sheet: Table 1
Created by Online2PDF.com
Part No. Item Description |  | SKU | Cost/Unit [$) | Quantity | Cost [$) | Supplier | Info
1 | Raspbeny Pi2 model B | 9SY1948 | 35.00 | 1 | 35 | Newark Element14
2 | Micro SD Card 8GD SD10 | SDSDQUAN-008G-G4A | 9.89 | 1 | 9.89 | Amazon.com
3 | Raspbeny PiTouchscreen | 49Y1712 | 60.00 | 1 | 60.00 | Newark Element14 | mouser
4 | 7nm collimatinglaser diodelens | BOOPPSJJ40 | 1.54 | 1 | 1.54 | Amazon.com
s | Raspbeny Picamera | 77Y6S21 | 18.50 | 1 | 18.5 | Newark Element14
6 | MX7 solenoid activated poppet valve | 961-712331-000 | 42.00 | 2 | 84.00 | Parker Hannifin Precision Fluidics
7 | Airtrol Regulator | V800-30 W/K | 36.30 | 2 | 72.60 | Hi-Tech Pneumatics
8 | Micro air pump | AP-2P01 | 65 | 1 | 65 | Smart producls
9 | 4-phase 5VDC unipolar stepper motor | 237825 | 9.95 | 1 | 9.95 | Jameco | from USA
10 | EasyDriver stepper motor driver | ROB-12779 | 14.9S | 1 | 14.95 | SparkFun | mouser
11 | Custom PCB | NIA | 25.00 | 1 | 25 | RoyalCircuit Solutions
12 | Honeywell TruStabilily pressure sensor | SSCDLNN01SPGAA5 | 32.87 | 2 | 65.74 | DigiKey
13 | DC/DC converter | V7805-2000R | 10.68 | 2 | 21.36 | DigiKey | mouser
14 | Solenoid driver DRV104 | 296-15746-1-ND | 5.62 | 2 | 11.24 | DigiKey | mouser
1S | LD1117V50-DG transistor (tC3 on PCB) | 497-12821-5-ND | 0.57 | 1 | 0.57 | DigiKey
16 | 68Kohm RES | PPC68.1KZTR-ND | O.52 | 4 | 2.08 | DigiKey | mouser
17 | 1uF CAP | 493-12567-3-ND | 0.11 | 2 | 0.22 | DigiKey | mouser
18 | 470pF CAP | 1286PH-ND | 0.25 | 2 | 0.50 | DigiKey
19 | 22ohm RES (RS on PCB) | CF14JT22ROCT-ND | 0.10 | 1 | 0.10 | DigiKey
20 | 2.1mm BarrelJack Connector | PRT-00119 | 1.25 | 1 | 1.25 | SparkFun | mouser
21 | MCP3008 | 856 | 3.75 | 1 | 3.75 | Adafruit | mouser
22 | 2N4401transistor | 2N4401D75ZCT-ND | 0.15 | 1 | 0.15 | DigiKey | mouser
23 | 40-PIN IDC connector | 2222 | 1.00 | 1 | 1.00 | Adafruit | mouser
24 | 1N4007 DIODE | 1N4007FSCT-ND | 0.09 | 2 | 0.18 | DigiKey | mouser
25 | Disc1 magnet N42 | D403 | 0.29 | 4 | 1.16 | K&J Magnetics | https://www.kjmagnetics.com/proddetail.asp?prod=D403 | Dimensions: 1/4" dia. x 3/32" thick
26 | Disc2 magnet N42 | D46 | 0.79 | 1 | 0.79 | K&J Magnetics | https://www.kjmagnetics.com/proddetail.asp?prod=D46 | Dimensions: 1/4" dia. x 3/8" thick
27 | SOW AC-to-DC switching power supply 12V 5A tabletop (small) | 1952370 | 18.95 | 1 | 18.95 | Jameco | from USA
28 | PLA 3D printing plastic (@ S41n50g or S41/9Sm) | Ultimaker PLA Black | 0.43 | 21.13 | 9.12 | fbrc8
29 | Cylinder magnet | D48-N52 | 1.28 | 1 | 1.28 | K&J Magnetics | https://www.kjmagnetics.com/proddetail.asp?prod=D48-N52 | Dimensions: 1/4" dia. x 1/2" thick
29.5 | USB Female Type A SMD Connector | PRT-09011 | 1.25 | 1 | 1.25 | SparkFun | mouser
30 | Machine screw 8-32.1/4" | 2094346 | 0.069 | 8 | 0.552 | Jameco | from USA
31 | Machine screw 8-32,112· | 106797 | 0.079 | 4 | 0.316 | Jameco | from USA
32 | Machine screw 4-40,112· | 106810 | 0.079 | 8 | 0.632 | Jameco | from USA
33 | Machine screw 2-56 x 1/4" | 38173 | 0.099 | 4 | 0.396 | Jameco | from USA
34 | Nut 8-32 | 51553 | 0.059 | 4 | 0.236 | Jameco | from USA
35 | Nut 4-40 | 40943 | 0.059 | 4 | 0.236 | Jameco | from USA
36 | Nut 2-56 | 38165 | 0.059 | 4 | 0.236 | Jameco | from USA
37 | Internal tooth washer #4 | 106850 | 0.059 | 2 | 0.118 | Jameco | from USA
38 | Flat washer #4 | 106826 | 0.065 | 2 | 0.13 | Jameco | from USA
39 | Hex standoff,male-female,8-32, 112", aluminum | 93505A452 | 0.56 | 4 | 2.24 | McMaster-Carr | Male-Female Threaded Hex Standoff, Aluminum, 1/4" Hex Size, 1/2" Long, 8-32 Thread Size
40 | Hex standoff,male-female,8-32, 314", aluminum | 93505A454 | 0.61 | 8 | 4.88 | McMaster-Carr | Male-Female Threaded Hex Standoff, Aluminum, 1/4" Hex Size, 3/4" Long, 8-32 Thread Size
41 | Round Standoff,female-female,8-32, 20.6mm or 0.812S" | 93330A457 | 0.54 | 4 | 2.16 | McMaster-Carr | Female Threaded Round Standoff, Aluminum, 1/4" OD, 3/4" Long, 8-32 Thread Size
42 | Spacer round, 4.75mm or 0.187" tall | 92510A421 | 0.27 | 2 | 0.54 | McMaster-Carr | Aluminum Unthreaded Spacer, 1/4" OD, 3/16" Long, for Number 4 Screw Size
43 | Thread to barn, 1/8-27NPT,7/16" Hex classic Bartl | 1810-6005 | 0.418 | 2 | 0.836 | Nordson Medical Value plastics | Threaded Fitting, 1/8-27 NPT Thread with 7/16" Hex to Classic Series Barb, 1/16" (1.6 mm) ID Tubing, Animal-Free Natural Polypropylene
44 | Tee tube fitting with 200 series barns,3132"(2.4 mm)ID | T220-2 | 0.246 | 4 | 0.984 | Nordson Medical Value plastics | Tube to Tube Fitting, Tee Tube Fitting with 200 Series Barbs, 3/32" (2.4 mm) ID Tubing, Black Nylon
45 | Elbow tube fitting with 200 series balbs,3132"(2.4 mm)ID | L220-2 | 0.246 | 21 | S.166 | Nordson Medical Value plastics | Tube to Tube Fitting, Elbow Tube Fitting with 200 Series Barbs, 3/32" (2.4 mm) ID Tubing, Black Nylon
46 | 3 Foot USB Data Sync and Power Charge Cable | 2135064 | 2.49 | 2 | 4.98 | Jameco | from USA
47 | Tygon tubing E-3603,3132" ID, S/32" OD | EW-06407-73 | 67 | 0.06 | 4.02 | Cole-Parmer
48 | USB flex lighi | BOOD2ZDY20 | 9.99 | 1 | 9.99 | Amazon.com
49 | 26G steel tubing 45 deg angle, 1·long | NE-236-304-1-45 |  | 5 |  | New England Small Tube | ?
50 | Buna N 0-ring,8mm x 2mm | 1RJD1 |  | 5 |  | McMaster-Carr
51 | 1.8 ml Cryo vials. internal threading | 363401PK |  |  |  | Thermofisher Scientific
S2 | 4.S m Cryo vials, internalthreading | 3634S2PK |  |  |  | Thermofisher Scientific
ITOTA L: $575.77 1

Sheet: Sheet1
Designator | Component | # | Cost per unit (USD) | Total cost (USD) | Source of materials | Material type
Hardware
M2 × 0.4 mm Thread × 12 mm Long Socket Head Screw | 91290A019 | 4 | $0.12 | $0.47 | McMaster-Carr | Steel
M2.5 × 0.45 mm Thread × 20 mm Long Socket Head Screw | 91290A108 | 8 | $0.28 | $2.24 | McMaster-Carr | Steel
M2.5 × 0.45 mm Thread × 10 mm Long Socket Head Screw | 91290A103 | 16 | $0.15 | $2.45 | McMaster-Carr | Steel
M2.5 × 0.45 mm Thread × 5 mm Philips Flat Head Screw | 92010A014 | 4 | $0.03 | $0.13 | McMaster-Carr | Steel
M3 × 0.5 mm Thread × 5 mm Long Socket Head Screw | 91290A110 | 8 | $0.08 | $0.66 | McMaster-Carr | Steel
M3 × 0.5 mm Thread × 20 mm Long Socket Head Screw | 91290A123 | 2 | $0.10 | $0.20 | McMaster-Carr | Steel
M5 × 0.8 mm Thread × 8 mm Long Socket Head Screw | 91290A222 | 12 | $0.09 | $1.08 | McMaster-Carr | Steel
M5 × 0.8 mm Thread × 15 mm Long Socket Head Screw | 91290A231 | 6 | $0.15 | $0.88 | McMaster-Carr | Steel
1/4″-20 Thread × 3/4″ Long Socket Head Screw | 5709A18 | 4 | $0.15 | $0.60 | McMaster-Carr | Steel
Compact End-Feed Fastener, M5, for 20 mm T-Slotted Framing | 5537T161 | 18 | $0.50 | $8.96 | McMaster-Carr | Steel
1.00″ × 1.00″ Smooth Surface T-Slotted Profile | 1010-S-Black-FB | 2 | $7.20 | $14.40 | 80/20 Inc. | Aluminum
Aluminum Sheet – 71 × 90 × 5 mm | 1247 | 1 | $21.42 | $21.42 | OnlineMetals | Aluminum
T8 Lead Screw + Copper Nut + Coupler + Pillow Block Bearings Lead Screw Set (300 mm) | KINGPRINT-KIT | 2 | $12.52 | $25.04 | Amazon | Steel
Linear Motion 8 mm Shaft × 330 mm Length | kit11868 | 2 | $15.18 | $30.36 | Amazon | Steel
Linear Bearing Ball Bushing | OS16211 | 2 | $1.21 | $2.43 | Amazon | Steel
Electronics
Raspberry Pi 3 – Model B – ARMv8 with 1G RAM | 3055 | 1 | $35.00 | $35.00 | Adafruit | Other | have
5 V 2.4A Switching Power Supply with 20AWG MicroUSB Cable | 1995 | 1 | $7.50 | $7.50 | Adafruit | Other | have
16 GB microSDHC Class 10 Flash Memory Card | 415,141 | 1 | $7.99 | $7.99 | Microcenter | Other | have
7″ Touch Screen for Raspberry Pi | B01ID5BQTC | 1 | $42.88 | $42.88 | Amazon | Other | have
Right HDMI Male to Left HDMI Male Cable | B06XT2JS1G | 1 | $7.99 | $7.99 | Amazon | Other
MOTORplate | MOTORR1 | 1 | $39.99 | $39.99 | Pi Plates | Other | bought
2.1 mm female/male barrel jack extension cable | 327 | 1 | $2.95 | $2.95 | Adafruit | Other
7.5 Volt 2.4 Amp Power Adapter | B006QYXFRO | 1 | $21.99 | $21.99 | Amazon | Other
Nema 14 Bipolar 1.8 deg 23Ncm 0.5A 7.5 V 35x35x42mm | 14HS17-0504S | 2 | $14.27 | $28.54 | StepperOnline | Other | which do I have?
Omron Snap Action Switch | COM-00098 | 2 | $1.95 | $3.90 | Sparkfun | Other
Heatsink 35 mm × 35 mm × 10 mm | B00MJVXB9K | 2 | $1.39 | $2.77 | Amazon | Aluminum
Heat Sink Thermal Tape 80 mm × 80 mm | 1468 | 1 | $4.50 | $4.50 | Adafruit | Other
Wire Assortment | 38,687 | 1 | $9.99 | $9.99 | Microcenter | Other
Heat Shrink Tubing Assortment | 544,023 | 1 | $2.99 | $2.99 | Microcenter | Other
Solder | 860,585 | 1 | $16.99 | $16.99 | Microcenter | Other
Optional
Aluminum Breadboard 12″ × 12″ × 1/2″, 1/4″-20 Taps | MB12 | 1 | $151.00 | $151.00 | Thorlabs | Aluminum
Slim Right-Angle Bracket with Counterbored Slot & 1/4″-20 Tapped Holes | AB90C | 4 | $26.25 | $105.00 | Thorlabs | Aluminum

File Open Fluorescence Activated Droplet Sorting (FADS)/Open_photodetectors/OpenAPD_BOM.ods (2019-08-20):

OpenAPD
 |  |  |  |  |  | Urs Gaudenz, GaudiLabs, 2017
Id | Quantity | Designator | Package | Designation | Mouser | Order
1 | 1 | D2 | LCC3_SMD | APD |  | 1 stock (digikey) | 2
26 | 1 | U3 | SOIC-08_N | OPA656 |  | 1 | 2
16 | 1 | U1 | QFN-12_4x4 | MAX1932 | 700-MAX1932ETCT | 1 | 2
21 | 1 | L1 | Choke_SMD_7.3x7.3_H3.5 | 250uH / 0.1A | 815-ASPI-0704S-271M | 1 | 2
20 | 1 | D3 | TOPLED | LED |  | stock (green high eff) | 2
19 | 1 | D1 | SMB_Handsoldering | 220V | 511-STTH1R04UY | 4 | 2
29 | 2 | N1,N2 | SOT-23 | BSS131 | BSS131 | stock | 4
2 | 1 | C1 | C_0805_HandSoldering | 1uF | 810-C2012X7R1C105K-3 | 4 | 2
3 | 1 | C2 | C_0805_HandSoldering | 0.047uF/200 V(smaller) | 810-C2012X7T2E473M1A | 4 | 2
4 | 1 | C3 | C_0805_HandSoldering | 0.1uF / 200V | 810-C2012X7T2E104MAA | 4 | 2
5 | 1 | C4 | C_0805_HandSoldering | 0.22uF |  | stock | 2
6 | 1 | C5 | C_0805_HandSoldering | 0.1uF |  | stock | 2
7 | 1 | C6 | C_0805_HandSoldering | 0.5-1pF |  | stock orded | 2 | 1pF
31 | 1 | TH1 | R_0805_HandSoldering | Thermistor_NTC 10k | 81-NCP21XV103J03RA | 10 | 2
22 | 1 | R11 | R_0805_HandSoldering | <1G Ohm | 279-RH73W2A1GNTN | 2+stock | 2 | 100m
30 | 1 | R12 | R_0805_HandSoldering | 10k |  | stock | 2
9 | 2 | R2,R3 | R_0805_HandSoldering | 1.2M (0) | 603-RC0805FR-071M2L | 10 | 4
8 | 1 | R1 | R_0805_HandSoldering | 4k |  | stock | 2 | 3.9k
10 | 1 | R4 | R_0805_HandSoldering | 3.3k |  | stock | 2
11 | 1 | R5 | R_0805_HandSoldering | 2.2M (1M) | 71-CRCW08052M20FKEA | 20 | 2
12 | 1 | R6 | R_0805_HandSoldering | 27k |  | stock | 2
13 | 1 | R7 | R_0805_HandSoldering |  |  | stock | 2
14 | 1 | R8 | R_0805_HandSoldering | 33k |  | stock | 2
15 | 2 | R9,R10 | R_0805_HandSoldering | 100k |  | stock | 4
23 | 1 | SW1 | PUSH_BUTTON_SMD | BUT |  | TASTER 9314 (reichelt) | 2
24 | 1 | SW2 | DC_JACK_SMD | DC_JACK |  | LUM 1613-14 (reichelt) | 2
25 | 1 | U2 | ARDUINO_MICRO_SMD | ARDUINO_MICRO |  | stock | 2

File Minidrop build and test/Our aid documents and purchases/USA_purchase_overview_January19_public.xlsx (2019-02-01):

company | arrived | nr_items | nr_unique_items | type | value | shipping | comment
smart products | may take 2-3 weeks | 2 | 1 | miniture airpumps with pins | 130.00 USD | 14.27 USD | enough for 2 instruments
McMaster Carr |  | 18 | 4 | metal stands threaded | 9.70 USD
Jameco |  | 75 | 12 | screws and nuts | 39.04 USD | 8.38 USD
KJ Magnetics | yes | 8 | 3 | small magnets | 5.30 USD | 5.00 USD
Parker |  | 4 | 1 | solenoid valves with pins | 178.50 USD | 10.00 USD | enough for 2 instruments
Coast Pneumatics |  | 4 | 1 | pressure regulators with pins | 191.00 USD | 15.95 USD | enough for 2 instruments
Combined shipping to DE |  |  |  |  |  | ?
 |  |  |  |  | TOTAL | TOTAL
 |  |  |  |  | 553.54 USD | 53.60 USD

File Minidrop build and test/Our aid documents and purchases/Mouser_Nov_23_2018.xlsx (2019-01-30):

WARENKORB
Dies ist keine Rechnung
23-Nov-18 07:24:29
 | Mouser-Nr. | Herst.- Nr. | Hersteller | Kunden-Teilenr | Beschreibung | RoHS | Lebenszyklus | Stückzahl | Preis (EUR) | Gesamtpreis: (EUR)
1 | 490-V7805-2000R | V7805-2000R | CUI Inc. |  | NICHT ISOLIERTE DC-DC-WANDLER Non-Isolated D C-DC Cnvrt | RoHS-konform |  | 2 | 8,86 € | 17.72 €
2 | 595-DRV104PWPR | DRV104PWPR | Texas Instruments |  | Motor / Bewegung / Zündungscontroller und Treiber High-Side Driver 1.5A | RoHS-konform |  | 2 | 3,92 € | 7.84 €
3 | 594-MRS25000C6812FRP | MRS25000C6812FRP00 | Vishay |  | Dünnfilmwiderstände - Durchgangsloch .6watt 68.1Kohms 1% 50ppm | RoHS-konform |  | 4 | 0,245 € | 0.98 €
4 | 647-UVK1H010MDD1TD | UVK1H010MDD1TD | Nichicon |  | Aluminium-Elektrolyt-Kondensatoren - Radial bedrahtet 1uF 50 Volts 20% | RoHS-konform | NRND | 2 | 0,192 € | 0.38 €
5 | 474-LCD-13733 | LCD-13733 | SparkFun Electronics |  | Sparkfun Raspberry Pi LCD - 7\" Touchscreen | RoHS-konform |  | 1 | 73,74 € | 73.74 €
6 | 512-2N4401TAR | 2N4401TAR | ON Semiconductor |  | Bipolartransistoren - BJT NPN Transistor General Purpose | RoHS-konform |  | 1 | 0,253 € | 0.25 €
7 | 750-1N4007T-G | 1N4007T-G | Comchip Technology |  | Gleichrichter 1A 1000V Rectifier Diode | RoHS-konform |  | 2 | 0,131 € | 0.26 €
8 | 474-PRT-00119 | PRT-00119 | SparkFun Electronics |  | SparkFun Zubehör DC Barrel Power Jack/Connector | RoHS-konform |  | 1 | 1,09 € | 1.09 €
9 | 485-856 | 856 | Adafruit |  | Adafruit Zubehör MCP3008 - 8-Channel 10-Bit ADC With SPI Interface | RoHS-konform |  | 1 | 3,27 € | 3.27 €
10 | 485-2222 | 2222 | Adafruit |  | Adafruit Zubehör GPIO Header for Raspberry Pi A+/B+/Pi 2/Pi 3 - 2x20 Female Header | RoHS-konform |  | 1 | 1,31 € | 1.31 €
11 | 474-ROB-12779 | ROB-12779 | SparkFun Electronics |  | IC-Entwicklungstools für Energieverwaltung EasyDriver - Stepper Motor Driver | RoHS-konform |  | 1 | 13,06 € | 13.06 €
12 | 474-PRT-09011 | PRT-09011 | SparkFun Electronics |  | SparkFun Zubehör USB Female Type A SMD Connector |  |  | 1 | 1,09 € | 1.09 €
Durch das Absenden Ihrer Bestellung erklären Sie sich mit diesen Geschäftsbedingungen einverstanden. (https://www.mouser.de/saleterms) |  |  |  |  |  |  |  |  | Gesamtwarenkosten: | 120.99
Die Preise sind zum angezeigten Datum und zur Uhrzeit reflektiert. |  |  |  |  |  |  |  |  | Versandkosten: | 0,00 €

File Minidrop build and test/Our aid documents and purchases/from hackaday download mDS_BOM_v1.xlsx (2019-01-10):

miniDrops_BOM (Bill of Materials)
William Stephenson
8/3/17 - added part 29.5, USB recepticle
 | Part No. | Item Description | Product No. | Unit Cost | Quantity | Cost [$] | Retailer
PRIMARY COMPONENTS | 1 | Raspberry Pi 2 model B | 95Y1948 | 35.00 | 1 | 35.00 | Newark Element14
 | 2 | Micro SD Card 8GD SD10 | SDSDQUAN-008G-G4A | 9.89 | 1 | 9.89 | Amazon.com
These are the primary components that drive the instrument. | 3 | Raspberry Pi Touchscreen | 49Y1712 | 60.00 | 1 | 60.00 | Newark Element14
 | 4 | 7mm collimating laser diode lens | B00PPSJJ40 | 1.54 | 1 | 1.54 | Amazon.com
 | 5 | Raspberry Pi camera | 77Y6521 | 18.50 | 1 | 18.50 | Newark Element14
 | 6 | mX7 Solenoid valve | SAMH000756/961-712321-000 | 42.00 | 2 | 84.00 | Parker Hannafin Precision Fluidics
 | 7 | Airtrol Regulator | V800-90 W/K | 36.30 | 2 | 72.60 | Hi-Tech Pneumatics
 | 8 | Micro air pump | AP-2P01 | 65.00 | 1 | 65.00 | Smart products
 | 9 | 4-phase 5VDC unipolar stepper motor | 237825 | 9.95 | 1 | 9.95 | Jameco
 | 10 | EasyDriver stepper motor driver | ROB-12779 | 14.95 | 1 | 14.95 | SparkFun
 | 11 | Custom PCB | N/A | 25.00 | 1 | 25.00 | Royal Circuit Solutions
 | 12 | Honeywell TruStability pressure sensor | SSCDLNN005PGAA5 | 32.87 | 2 | 65.74 | DigiKey
 | 13 | DC/DC converter | V7805-2000R | 10.68 | 2 | 21.36 | DigiKey
 | 14 | Solenoid driver DRV104 | 296-15746-1-ND | 5.62 | 2 | 11.24 | DigiKey
 | 15 | LDV33 transistor | 497-1491-5-ND | 0.56 | 1 | 0.56 | DigiKey
 | 16 | 68Kohm RES | PPC68.1KZTR-ND | 0.52 | 4 | 2.08 | DigiKey
 | 17 | 1uF CAP | 493-12567-3-ND | 0.11 | 2 | 0.22 | DigiKey
 | 18 | 470pF CAP | 1286PH-ND | 0.25 | 2 | 0.50 | DigiKey
 | 19 | 220ohm RES | CF12JT220RCT-ND | 0.04 | 1 | 0.04 | DigiKey
 | 20 | 2.1mm Barrel Jack Connector | PRT-00119 | 1.25 | 1 | 1.25 | SparkFun
 | 21 | MCP3008 | 856 | 3.75 | 1 | 3.75 | Adafruit
 | 22 | 2N4401 transistor | 2N4401D75ZCT-ND | 0.15 | 1 | 0.15 | DigiKey
 | 23 | 40-PIN IDC connector | 2222 | 1.00 | 1 | 1.00 | Adafruit
 | 24 | 1N4007 DIODE | 1N4007FSCT-ND | 0.09 | 2 | 0.18 | DigiKey
 | 25 | Disc1 magnet N42 | D403 | 0.29 | 4 | 1.16 | K&J Magnetics
 | 26 | Disc2 magnet N42 | D46 | 0.79 | 1 | 0.79 | K&J Magnetics
 | 27 | 60W AC-to-DC switching table-top power supply 12V 5A | 1952370 | 18.95 | 1 | 18.95 | Jameco
 | 28 | PLA 3D printing plastic (@ $41/750g or $41/95m) | Ultimaker PLA Black (https://fbrc8.com/products/ultimaker-pla-black) | 0.43 | 21.13 | 9.12 | fbrc8
 | 29 | Cylinder magnet | D48-N52 (https://www.kjmagnetics.com/proddetail.asp?prod=D48-N52) | 1.28 | 1 | 1.28 | K&J Magnetics
 | 29.5 | USB Female Type A SMD Connector | PRT-09011 | 1.25 | 1 | 1.25 | SparkFun
MISCELLANEOUS COMPONENTS | 30 | Machine screw 8-32, 1/4" | 2094346 | 0.069 | 8 | 0.552 | Jameco
 | 31 | Machine screw 8-32, 1/2" | 106797 | 0.079 | 4 | 0.316 | Jameco
For most of these items you many want to order a few extra just in case you lose some as these are small parts. Unfortunately for some of the other parts there are minimum order quantity so you definatley will have leftovers unless you have some on hand already or find a substitute retailer. A majority of these parts can be found in a University machine shop or engineering lab. | 32 | Machine screw 4-40, 1/2" | 106810 | 0.079 | 8 | 0.632 | Jameco
 | 33 | Machine screw 2-56 x 1/4" | 38173 | 0.099 | 4 | 0.396 | Jameco
 | 34 | Nut 8-32 | 51553 | 0.059 | 4 | 0.236 | Jameco
 | 35 | Nut 4-40 | 40943 | 0.059 | 4 | 0.236 | Jameco
 | 36 | Nut 2-56 | 38165 | 0.059 | 4 | 0.236 | Jameco
 | 37 | Internal tooth washer #4 | 106850 | 0.059 | 2 | 0.118 | Jameco
 | 38 | Flat washer #4 | 106826 | 0.065 | 2 | 0.13 | Jameco
 | 39 | Hex standoff, male-female, 8-32, 1/2", aluminum | 93505A452 (https://www.mcmaster.com/) | 0.56 | 4 | 2.24 | McMaster-Carr
 | 40 | Hex standoff, male-female, 8-32, 3/4", aluminum | 93505A454 | 0.61 | 8 | 4.88 | McMaster-Carr
 | 41 | Round Standoff, female-female, 8-32, 20.6mm or 0.8125" | 93330A457 | 0.54 | 4 | 2.16 | McMaster-Carr
 | 42 | Spacer round, 4.75mm or 0.187" tall | 92510A421 | 0.27 | 2 | 0.54 | McMaster-Carr
 | 43 | Thread to barb, 1/8-27NPT, 7/16" Hex classic Barb | 1810-6005 | 0.418 | 2 | 0.836 | Nordson Medical/Value plastics
 | 44 | Tee tube fitting with 200 series barbs, 3/32" (2.4 mm) ID | T220-2 | 0.246 | 4 | 0.984 | Nordson Medical/Value plastics
 | 45 | Elbow tube fitting with 200 series barbs, 3/32" (2.4 mm) ID | L220-2 | 0.246 | 21 | 5.166 | Nordson Medical/Value plastics
 | 46 | 3 Foot USB Data Sync and Power Charge Cable | 2135064 | 2.49 | 2 | 4.98 | Jameco
 | 47 | Tygon tubing E-3603, 3/32" ID, 5/32" OD | EW-06407-73 | 67 | 0.06 | 4.02 | Cole-Parmer
 | 48 | USB flex light | B00D2ZDY2Q | 9.99 | 1 | 9.99 | Amazon.com
 | 49 | 26G steel tubing 45 deg angle, 1" long | NE-236-304-1-45 | - | 5 | - | New England Small Tube
 | 50 | Buna N O-ring, 8mm x 2mm | 1RJD1 | - | 5 | - | McMaster-Carr
 | 51 | 1.8 mL Cryo vials, internal threading | 363401PK | - | - | - | Thermofisher Scientific
 | 52 | 4.5 mL Cryo vials, internal threading | 363452PK | - | - | - | Thermofisher Scientific
 |  |  |  | Approx. GRAND TOTAL: |  | $575.70

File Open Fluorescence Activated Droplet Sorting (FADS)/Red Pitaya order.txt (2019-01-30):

Red Pitaya ultimate stem lab pack ordered at Reichelt Germany on the 17th January 2019 for 562,61 Euro

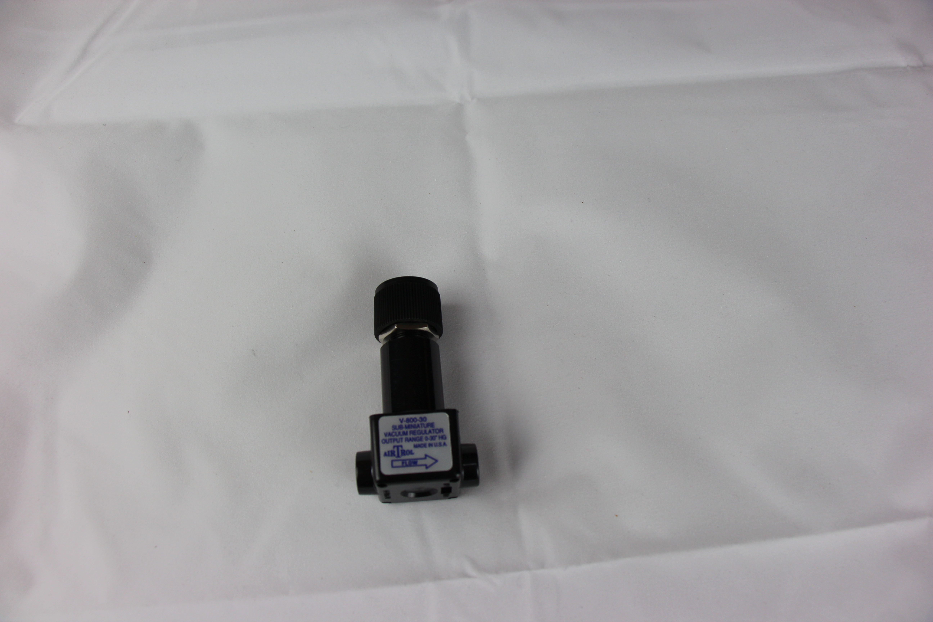
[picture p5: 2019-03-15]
Minidrop build and test/minidrop_component_photos/IMG_4487_CR2_embedded.jpg

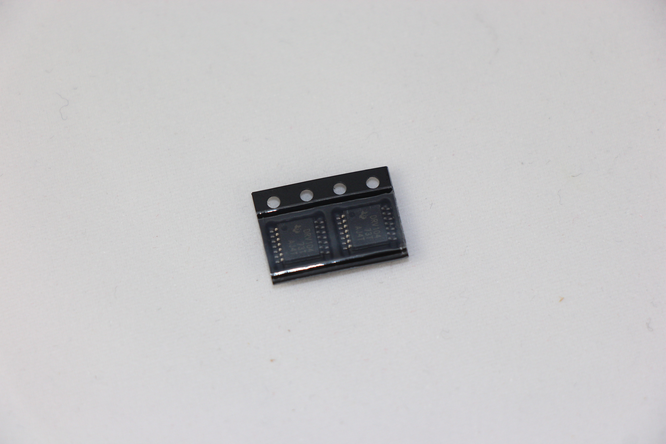
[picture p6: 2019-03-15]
Minidrop build and test/minidrop_component_photos/IMG_4546_CR2_embedded.jpg

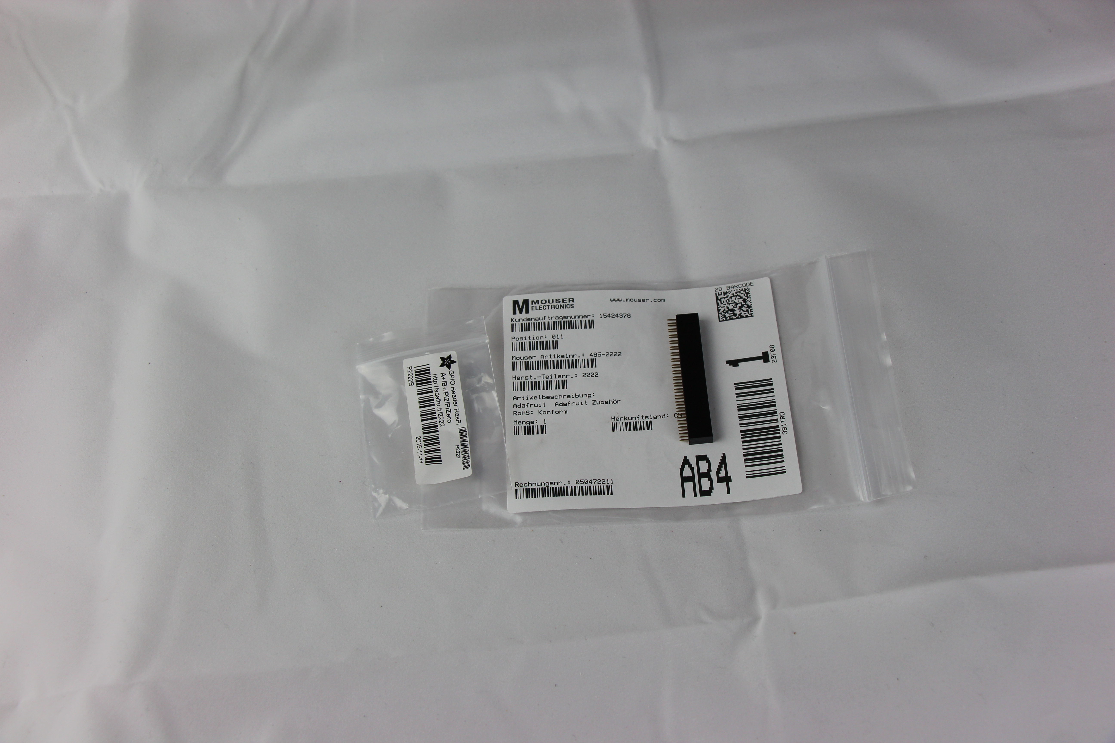
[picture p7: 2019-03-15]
Minidrop build and test/minidrop_component_photos/IMG_4526_CR2_embedded.jpg

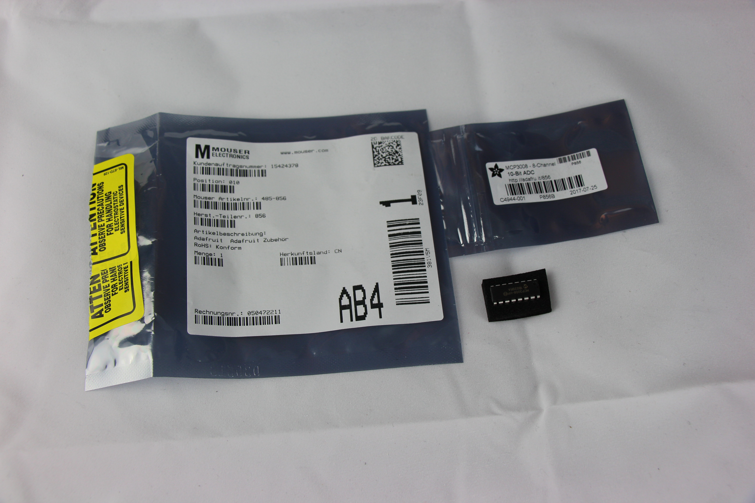
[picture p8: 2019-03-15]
Minidrop build and test/minidrop_component_photos/IMG_4543_CR2_embedded.jpg

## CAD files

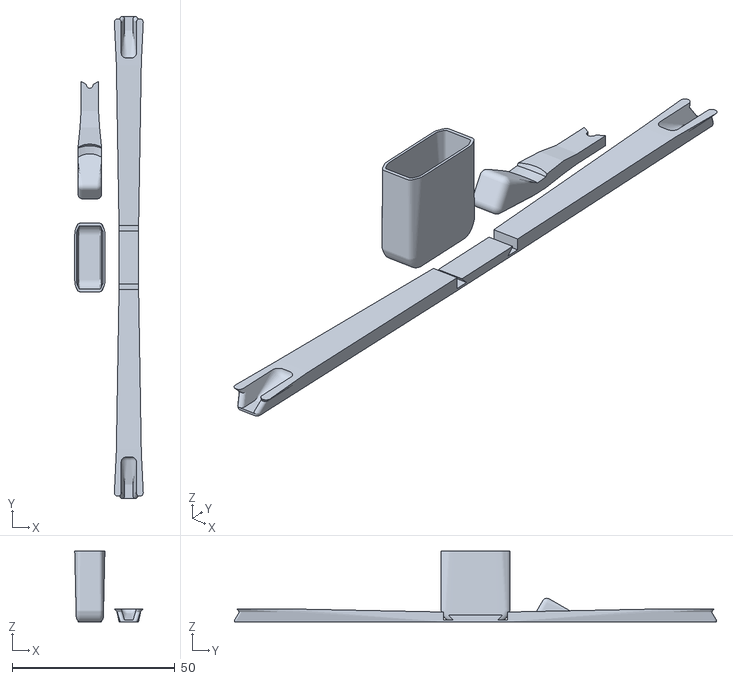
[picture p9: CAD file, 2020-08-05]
OpenFlexure Fluorescence Microscope/STL files/actuator_assembly_tools.stl
21.1 x 148.2 x 21.7

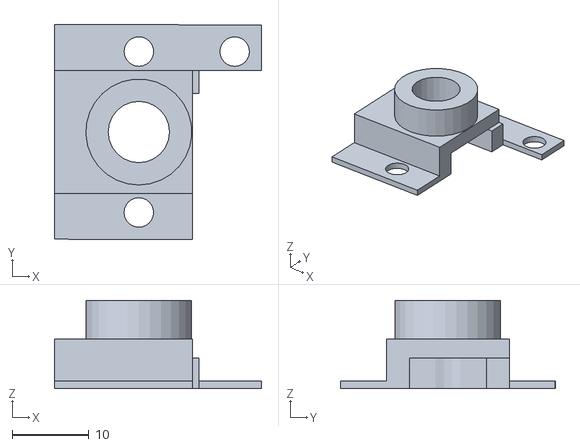
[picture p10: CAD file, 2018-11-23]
Minidrop build and test/Original files/3d_printed_parts/mDS_lensmount.stl
27.0 x 28.0 x 11.5

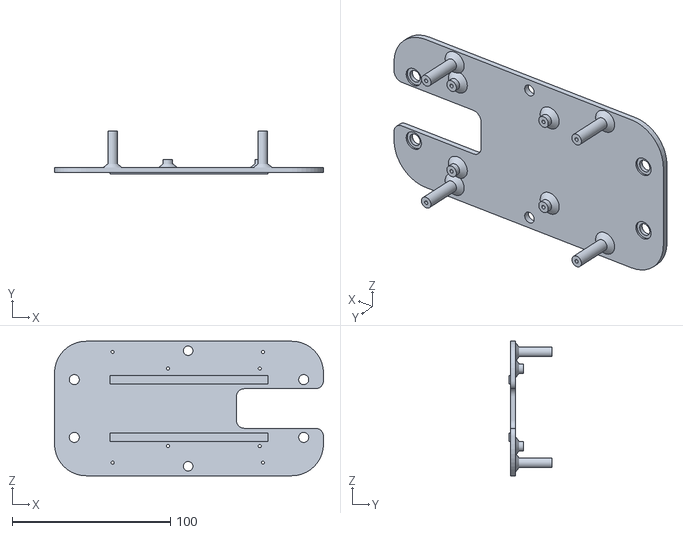
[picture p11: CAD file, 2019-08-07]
Open Syringe Pump/dual syringepump build and test/stl_parts_3d_printing/pi_base_v6.STL
170.0 x 27.0 x 85.0

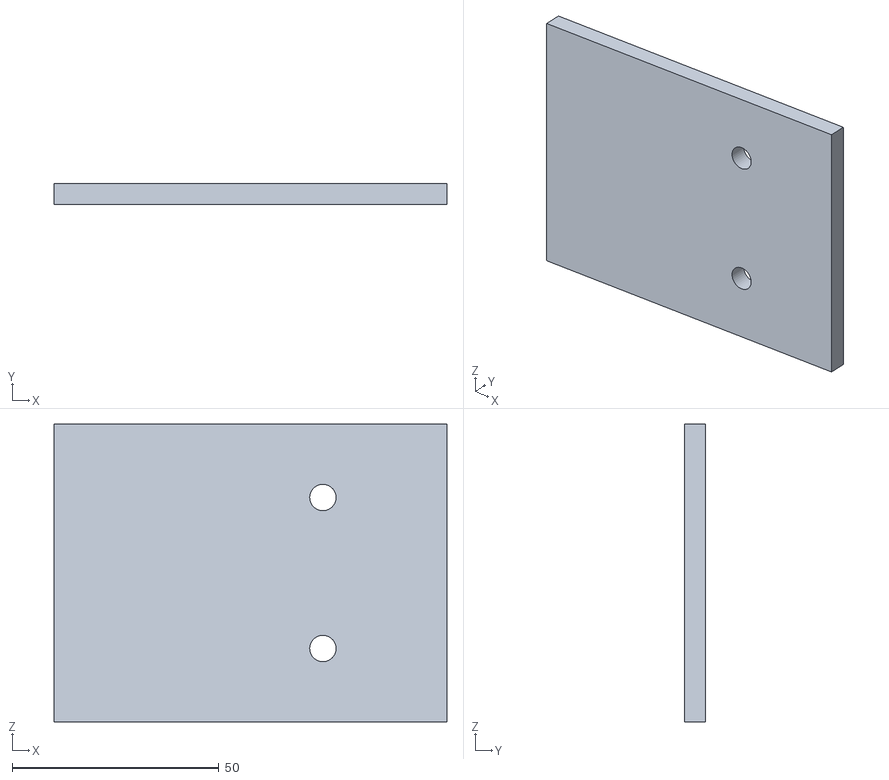
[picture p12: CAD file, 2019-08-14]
Open Syringe Pump/dual syringepump build and test/SupplementalFile-S1-HeatSink_V2.STL
95.0 x 5.00 x 72.0

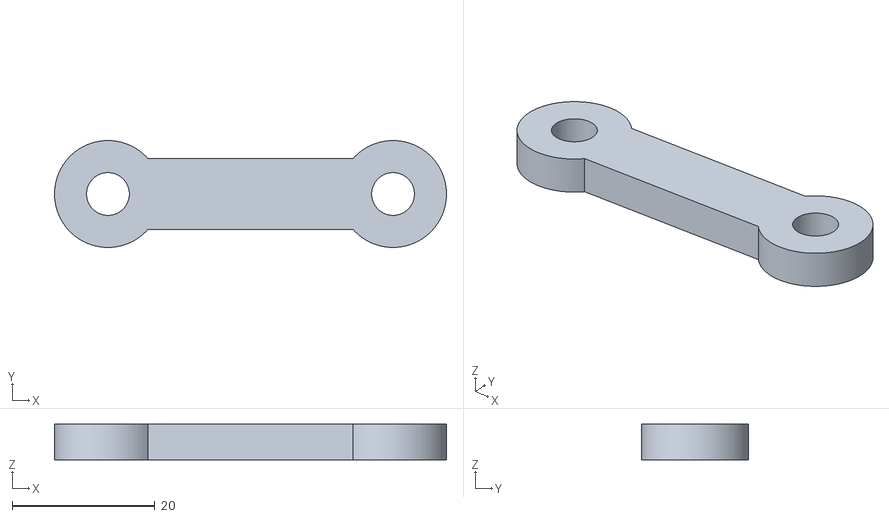
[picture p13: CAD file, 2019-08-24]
Open Syringe Pump/Open Source Syringe Pump Library, PLOS ONE 2014/source files syringepump/linear_actuator_v0-8.stl
55.0 x 15.0 x 5.00

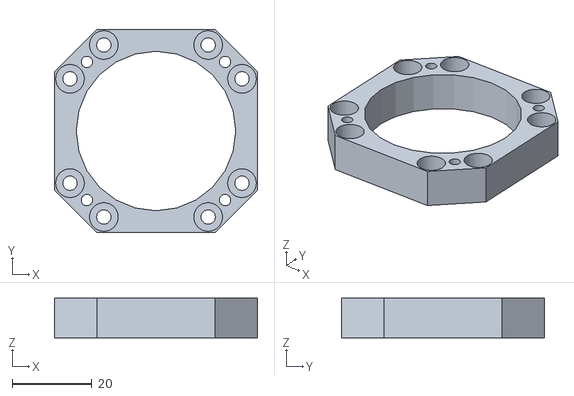
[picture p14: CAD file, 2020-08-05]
OpenFlexure Fluorescence Microscope/STL files/sample_riser_LS10.stl
50.9 x 50.9 x 10.0

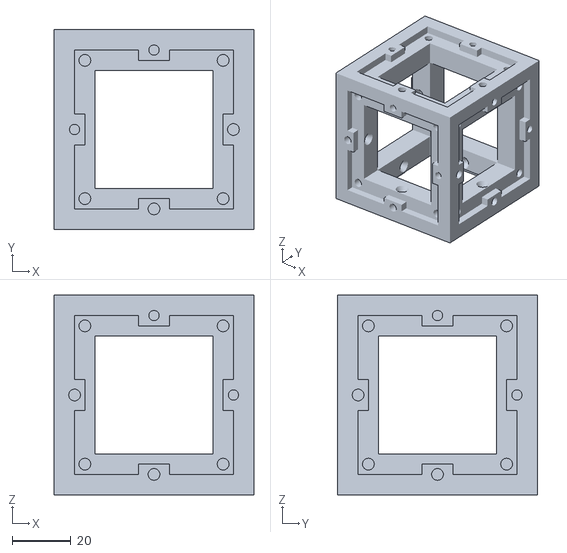
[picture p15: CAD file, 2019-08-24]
OpenFlexure Fluorescence Microscope/uCube/uCube.stl
68.0 x 68.0 x 68.0

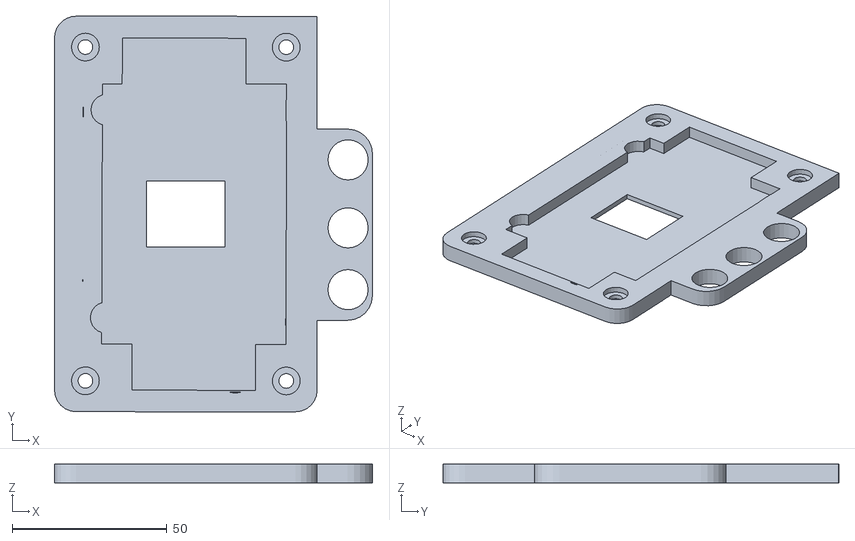
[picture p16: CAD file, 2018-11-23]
Minidrop build and test/Original files/3d_printed_parts/mDS_top.stl
102.9 x 128.0 x 6.00

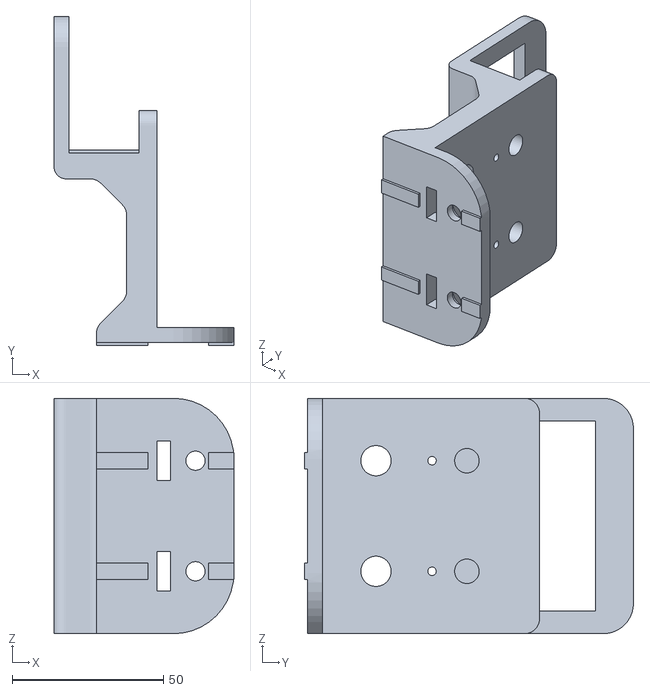
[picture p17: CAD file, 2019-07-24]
Open Syringe Pump/dual syringepump build and test/stl_parts_3d_printing/extractmaker_holder_v4.STL
59.4 x 108.6 x 77.7

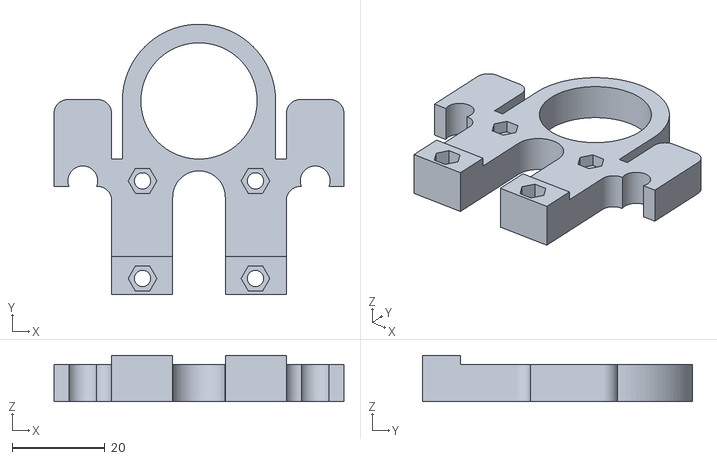
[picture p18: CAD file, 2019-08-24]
Open Syringe Pump/Open Source Syringe Pump Library, PLOS ONE 2014/source files syringepump/linear_actuator_v0-5.stl
62.4 x 58.2 x 10.0

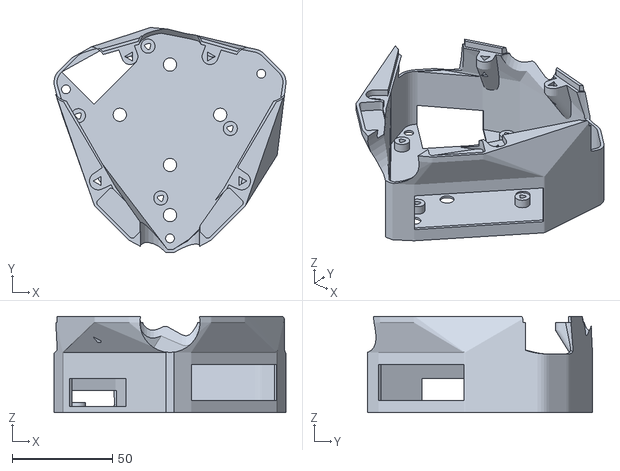
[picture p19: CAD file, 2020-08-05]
OpenFlexure Fluorescence Microscope/STL files/microscope_stand_30-BS.stl
115.6 x 112.1 x 48.0

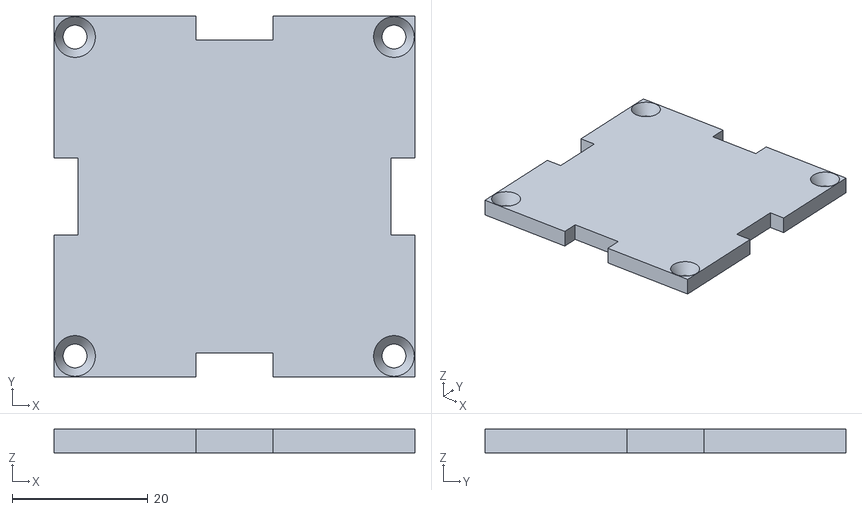
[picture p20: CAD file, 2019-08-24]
OpenFlexure Fluorescence Microscope/uCube/uFace.stl
53.2 x 53.2 x 3.50

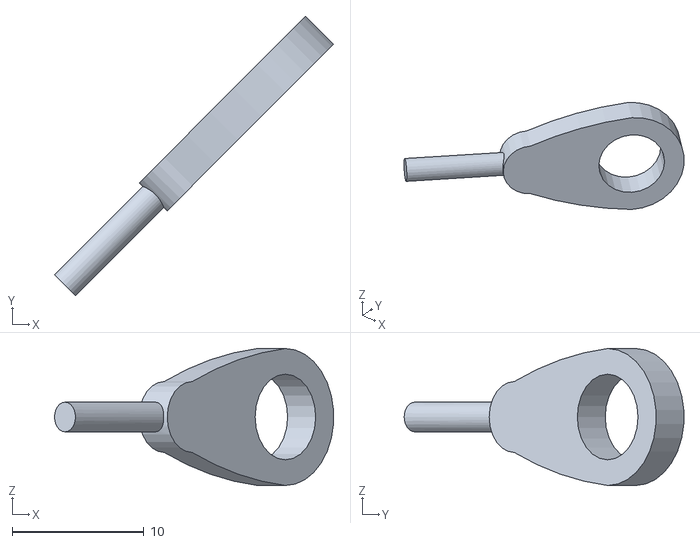
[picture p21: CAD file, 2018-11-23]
Minidrop build and test/Original files/3d_printed_parts/mDS_maghold.stl
21.2 x 21.2 x 10.4

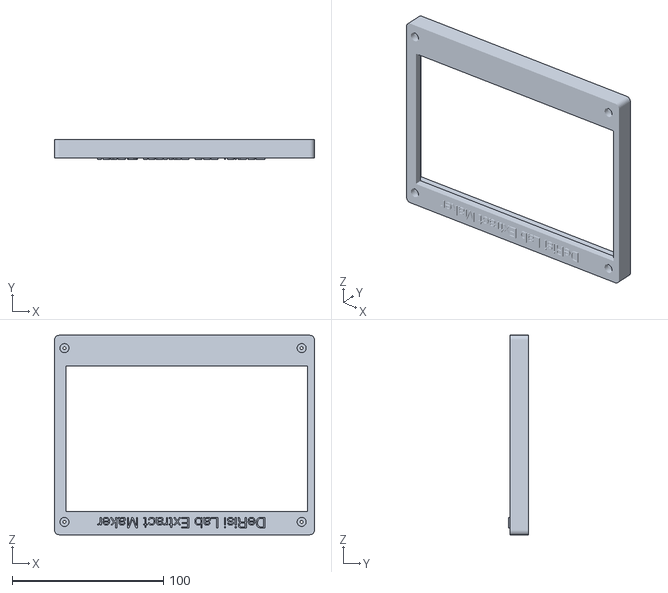
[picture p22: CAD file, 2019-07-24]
Open Syringe Pump/dual syringepump build and test/stl_parts_3d_printing/screen_cover_v2.STL
172.0 x 13.0 x 132.0

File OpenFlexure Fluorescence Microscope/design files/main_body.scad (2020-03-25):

/******************************************************************
*                                                                 *
* OpenFlexure Microscope: Microscope body                         *
*                                                                 *
* This is the chassis of the OpenFlexure microscope, an open      *
* microscope and 3-axis translation stage.  It gets really good   *
* precision over a ~10mm range, by using plastic flexure          *
* mechanisms.                                                     *
*                                                                 *
* (c) Richard Bowman, January 2016                                *
* Released under the CERN Open Hardware License                   *
*                                                                 *
******************************************************************/

use <./utilities.scad>;
use <./compact_nut_seat.scad>;
use <./logo.scad>;
use <./dovetail.scad>;
use <./z_axis.scad>;
use <./gears.scad>;
use <./wall.scad>;
use <./main_body_transforms.scad>;
use <./reflection_illuminator.scad>;
include <./microscope_parameters.scad>; //All the geometric variables are now in here.


module leg(brace=stage_flex_w){
    // The legs support the stage - this is either used directly
    // or via "actuator" to make the legs with levers
    fw=stage_flex_w;
	union(){
       	//leg
		reflect([1,0,0]){
			//vertical legs
			translate([leg_middle_w/2+zflex_l,0,0]) hull(){
				cube(leg);
				cube([leg[0],fw+brace,d]); //extend it to be a triangle
			}

            //flexure bridges between the legs
            zs = [flex_z1, flex_z2]; //heights of bridges between legs
            bs = [brace, 0]; //"brace positions" - a nonzero value here
                             //widens the leg, and adds another flexure
                             //at the new position.  bs[i]=fw will double
                             //the width of the flexure, while a larger 
                             //value produces two distinct flexures.
			for(i=[0,1]) translate([0,0,zs[i]]){
				translate([-d,0,0]) hull() repeat([0,bs[i],0],2) //solid part
                        cube([leg_middle_w/2+d,leg[1],stage_t-0.2*leg[1]]);
				translate([-d,0,0]) repeat([0,bs[i],0],2) //flexures
                        cube([leg_middle_w/2+zflex_l+leg[0],leg[1],zflex_t]);
			}
		}
        
		//thin links between legs
		if(flex_z2-flex_z1 > 2*bridge_dz){
			n=floor((flex_z2-flex_z1)/bridge_dz);
			dz=(flex_z2-flex_z1)/n;
			translate([0,leg[1]/2,flex_z1+dz]) repeat([0,0,dz],n-1) cube([leg_outer_w,2,0.5],center=true);
		}
	}
}
module actuator(){
    // A leg that supports the stage, plus a lever to tilt it.
    // No longer includes the flexible nut seat actuating column.
    // TODO: find the code that unifies this with leg()
	brace=20;
    fw=stage_flex_w;
    w = actuator[0];
    union(){
        leg(brace=brace);

		//arm (horizontal bit)
		difference(){
            sequential_hull(){
                translate([-leg_middle_w/2,0,0]) cube([leg_middle_w,brace+fw,4]);
                translate([-w/2,0,0]) cube([w,brace+fw+0,actuator[2]]);
                translate([-w/2,0,0]) cube(actuator);
            }
            //don't foul the actuator column
            translate([0,actuating_nut_r,0]) actuator_end_cutout(); 
        }

	}
}
module actuator_silhouette(h=999){
    // This defines the cut-out from the base structure for the XY
    // actuators.
    linear_extrude(2*h,center=true) minkowski(){
        circle(r=zflex_l,$fn=12);
        projection() actuator();
    }
}

module back_foot_mounting_screw(d=3*0.95, h=16, center=true){
    translate([0,illumination_clip_y+3,0]) cylinder(d=d, h=h,center=center);
}

module mounting_hole_lugs(){
    // lugs either side of the XY table to bolt the microscope down
    //these are to mount onto the baseplate 
    for(p=base_mounting_holes) {
        if(p[1]<0 && p[0]>0) reflect([1,0,0]) hull(){
            translate([z_flexure_x,0,0]) rotate(-120) cube([10,d,10]);
            translate(p) cylinder(r=4*1.1,h=3);
        }
    }
}

module xy_limit_switch_mount(d=3.3*2, h=6){
    // A mount for the XY limit switch (M3)
    leg_frame(45) translate([-9, -zflex_l-zawall_h*sin(6)-3.3+1, zawall_h-6]) cylinder(d=d,h=h);
}


// The "wall" that forms most of the microscope's structure
module wall_inside_xy_stage(beamsplitter=false){
    front_wall_height = beamsplitter ? zawall_h : wall_h;
    // First, go around the inside of the legs, under the stage.
    // This starts at the Z nut seat.  I've split it into two
    // blocks, because the shape is not convex so the base
    // would be bigger than the walls otherwise.
    reflect([1,0,0]) sequential_hull(){
        //inner_wall_vertex(-45, -leg_outer_w/2-wall_t/2, zbwall_h);
        mirror([1,0,0]) z_bridge_wall_vertex();
        z_bridge_wall_vertex();
        inner_wall_vertex(45, -leg_outer_w/2, zawall_h);
        z_anchor_wall_vertex();
        inner_wall_vertex(135, leg_outer_w/2, zawall_h);
        inner_wall_vertex(135, -leg_outer_w/2, front_wall_height);
        inner_wall_vertex(-135, leg_outer_w/2, front_wall_height);
    };    

}

module wall_outside_xy_actuators(){
    // Add the wall from the XY actuator column to the middle
    sequential_hull(){
        z_anchor_wall_vertex(); // join at the Z anchor 
        // [nb this is no longer actually the z anchor since the new z axis]
        // anchor at the same angle on the actuator
        // NB the base of the wall is outside the
        // base of the screw seat
        leg_frame(45) translate([-ss_outer()[0]/2+wall_t/2,actuating_nut_r,0]){
            rotate(-45) wall_vertex(y_tilt=atan(wall_t/zawall_h));
        }
    }
}

module wall_inside_xy_actuators(){
    // Connect the Z anchor to the XY actuators
    hull(){
        translate([-(z_anchor_w/2+wall_t/2+1), z_anchor_y + 1, 0]) 
                     wall_vertex();
        y_actuator_wall_vertex();
    }
}

module wall_between_actuators(){
    // link the actuators together
    hull(){
        y_actuator_wall_vertex();
        translate([0,z_nut_y+ss_outer()[1]/2-wall_t/2,0]) wall_vertex();
    }
}

// Cut out hole for reflection illuminator
module fl_cube_cutout(){
    // size of cutout for fl cube
    top_cutout_w = 17.8; // As big as we can get at height 'wall_h' without bridging a corner
    mid_cutout_w = illuminator_width() + 1;
    bottom_cutout_w = illuminator_width() + 4;

    // Create a trapezoid with min width (cube_width) at top
    hull() {
        translate([-(bottom_cutout_w)/2, -49, -0.5]) cube([bottom_cutout_w, 49, 1]);
        translate([-(mid_cutout_w)/2, -49, 10]) cube([mid_cutout_w, 49, 1]); // Highest we usually need
        translate([-top_cutout_w/2, -49, wall_h]) cube([top_cutout_w, 49, 1]);
    }
}

///////////////////// MAIN STRUCTURE STARTS HERE ///////////////
exterior_brim(r=enable_smart_brim ? smart_brim_r : 0)
difference(){
union(){

	//legs (incl. actuators)
	reflect([1,0,0]) leg_frame(135) leg();
	each_actuator(){
        actuator();
		translate([0,actuating_nut_r,0]) actuator_column(h=actuator_h, join_to_casing=true);
    }
	//flexures connecting bottoms of legs to centre
	each_leg() reflect([1,0,0]) translate([0,0,flex_z1]){
        w=stage_flex_w;
        translate([leg_middle_w/2-w,0,0.5]) hull()
			repeat([1,-1,0]*(zflex_l+wall_t/2),2) cube([w,d,zflex_t]);
    }
    //tie the legs to the wall (built later) during printing
    reflect([1,0,0]) leg_frame(135) reflect([1,0,0]) {
        translate([leg_middle_w/2+zflex[1]+zflex[0]/2, -wall_h*0.7*tan(6)-1-zflex[1], wall_h*0.7]) cube([1, wall_h*0.7*tan(6)+2+zflex[1], 0.5]);
    }

	// flexures between legs and stage
    // NB these connect the legs together, and pass all the way under the stage.  This
    // is important, if they get cut then the bridges will fail!
	difference(){
		hull() each_leg() translate([0,0,flex_z2+zflex_t/2+0.5]) cube([leg_middle_w,d,zflex_t],center=true);
		hull() each_leg() cube([leg_middle_w-2*stage_flex_w,d,999],center=true);
	}

	//stage
   // this must get built up carefully: we start with the bridges round the edge, then work inwards.
	difference(){
		hull() each_leg() translate([0,-zflex_l-d,flex_z2+1+(stage_t-1)/2]) cube([leg_middle_w+2*zflex_l,2*d,stage_t-1],center=true); //hole in the stage
        intersection(){
            // This cuts out the hole in the stage, starting from a square.
            // The intersection restricts it to the space between the bridges, to avoid any
            // holes in the sides of the stage.
            translate([0,0,flex_z2+0.5+0.5]) rotate(45) hole_from_bottom(hole_r,h=999);
            hull() each_leg() cube([leg_middle_w-2*stage_flex_w,d,999],center=true);
        }
		each_leg() translate([0,-zflex_l-4,flex_z2+1.5]) repeat([leg_middle_w/2,0,0],3,center=true) trylinder_selftap(3,h=999); //mounting holes
	}
	
	//z axis
    z_axis_flexures();
    z_axis_struts();
    objective_mount();
    z_actuator_column();
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

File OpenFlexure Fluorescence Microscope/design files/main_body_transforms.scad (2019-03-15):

/******************************************************************
*                                                                 *
* OpenFlexure Microscope: Microscope body transforms              *
*                                                                 *
* Various transforms used in the microscope.                      *
*                                                                 *
* (c) Richard Bowman, January 2016                                *
* Released under the CERN Open Hardware License                   *
*                                                                 *
******************************************************************/

use <./utilities.scad>;
use <./compact_nut_seat.scad>;
include <./microscope_parameters.scad>;

module shear_x(amount=1){
    // Shear transformation: tilt the Y axis towards the X axis
    // e.g. if amount=1, then a straight line in Y will be
    // tilted to 45 degrees between X and Y, while X lines are
    // unchanged.  This is used in the Z axis.
	multmatrix([[1,amount,0,0],
					 [0,1,0,0],
					 [0,0,1,0],
					 [0,0,0,1]]) children();
}


module leg_frame(angle){
    // Transform into the frame of one of the legs of the stage
	rotate(angle) translate([0,leg_r,]) children();
}
module each_leg(){
    // Repeat for each of the legs of the stage
	for(angle=[45,135,-135,-45]) leg_frame(angle) children();
}
module each_actuator(){
    // Repeat this for both of the actuated legs (the ones with levers)
	reflect([1,0,0]) leg_frame(45) children();
}

module place_on_wall(){
    //this is a complicated transformation!  The wall runs from
    wall_start = [z_flexure_x+wall_t/2,-wall_t/2,0]; // to
    wall_end = ([1,1,0]*(leg_r+actuating_nut_r)
                 +[1,-1,0]*(ss_outer()[0]/2-wall_t/2))/sqrt(2);
    wall_disp = wall_end - wall_start; // vector along the wall base
    // pivot about the starting corner of the wall so X is along it
    translate(wall_start) rotate(atan(wall_disp[1]/wall_disp[0]))
    // move out to the surface (the above are centres of cylinders)
    // and then align y with the vertical axis of the wall
    translate([0,-wall_t/2,0]) rotate([90-atan(wall_t/zawall_h/sqrt(2)),0,0])
    // now X and Y are in the plane of the wall, and z=0 is its surface.
    children();
}

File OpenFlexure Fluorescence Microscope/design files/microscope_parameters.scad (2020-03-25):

/******************************************************************
*                                                                 *
* OpenFlexure Microscope: Microscope Parameters                   *
*                                                                 *
* This is the top-level configuration file for the OpenFlexure    *
* microscope, an open microscope and 3-axis translation stage.    *
* It gets really good precision over a ~10mm range, by using      *
* plastic flexure mechanisms.                                     *
*                                                                 *
* Generally I've tried to put parts (or collections of closely    *
* related parts) in their own files.  However, all the parts      *
* depend on the geometry of the microscope - so these parameters  *
* are gathered together here.  In general, the ones you might     *
* to change are towards the top!  Lower-down ones are defined in  *
* terms of higher-up ones - confusion might arise if you redefine *
* these later...                                                  *
*                                                                 *
* (c) Richard Bowman, January 2016                                *
* Released under the CERN Open Hardware License                   *
*                                                                 *
* http://www.github.com/rwb27/openflexure_microscope              *
* http://www.docubricks.com/projects/openflexure-microscope       *
* http://www.waterscope.org                                       *
*                                                                 *
******************************************************************/

d = 0.05;
$fn=32;

// These are the most useful parameters to change!
big_stage = true; //this option is obsolete and must now always be true...
motor_lugs = true;
version_numstring = "6.0.0";
camera = "picamera_2"; //see cameras/camera.scad for valid values
optics = "rms_f50d13"; //see optics.scad for valid values
led_r = 4.5/2; //size of the LED used for illumination
endstops = false; //whether to build mounts for optical endstops inside the microscope.
feet_endstops = false; //whether to include cut-outs for endstop switches in the feet. 
beamsplitter = false; //enables a cut-out in some optics modules for a beamsplitter
smart_brim_r = 5;
enable_smart_brim = false;

// This sets the basic geometry of the microscope
sample_z = big_stage?65:40; // height of the top of the stage
leg_r = big_stage?30:25; // radius of innermost part of legs (stage size)
hole_r = big_stage?20:10; // size of hole in the stage
xy_lever_ratio = big_stage?4.0/7.0:1.0; // mechanical advantage of actuator over stage - can be used to trade speed and precision
z_lever_ratio = 1.0; // as above, for Z axis (must be >1)
// The variables below affect the position of the objective mount
z_strut_l = big_stage?18:15; //length of struts supporting Z carriage
objective_mount_y = big_stage?18:12; // y position of clip for optics
objective_mount_nose_w = 6; // width of the pointy end of the mount
condenser_clip_w = 14; // width of the dovetail clip for the condenser
foot_height=feet_endstops?15:15; //the endstops need a bit of extra height (or not)

// These variables set the dimensions of flexures
// You might want to tweak them if your material (or printer)
// is different from the ones I've tested, though ABS/PLA extrusion
// is generally fine with my parameters
stage_flex_w = 4; // width of XY axis flexures
zflex_l = 1.5;    // length of (all) flexible bits
zflex_t = 0.75;   // thickness of (all) flexible bits
zflex = [stage_flex_w, zflex_l, zflex_t]; // the above in new-style format
flex_a = 0.15;    // sine of the angle through which flexures can be bent

// Compile a sensible version string
version_string = str("v",version_numstring, big_stage?"-LS":"-SS", sample_z, motor_lugs?"-M":"");
echo(str("Compiling OpenFlexure Microscope ",version_string));

stage_t=5; //thickness of the XY stage (at thickest point, most is 1mm less)
flex_z1 = 0;      // z position of lower flexures for XY axis
flex_z2 = sample_z-stage_t; //height of upper XY flexures
z_strut_t = 6;  // (z) thickness of struts for Z axis
z_flex_w = 4;   // width of struts for Z axis
leg = [4,stage_flex_w,flex_z2+zflex_t]; // size of vertical legs
leg_middle_w = 12; // width of the middle part of each leg
actuator_h = 25; //height of the actuator columns
dz = 0.5; //small increment in Z (~ 2 layers)

leg_outer_w = leg_middle_w + 2*zflex_l + 2*leg[0]; // overall width of parallelogram legs that support the stagef
actuator = [3*1.2+2*2,(flex_z2 - flex_z1)*xy_lever_ratio,6]; // dimensions of the core part of the actuating levers for X and Y - NB should match the column_base_r in compact_nut_seat.scad
actuating_nut_r = (flex_z2 - flex_z1)*xy_lever_ratio; // distance from leg_r to the actuating nut/screw for the XY axes
xy_actuator_travel = actuating_nut_r*0.15; // distance moved by XY axis actuators

// Z axis
z_flexures_z1 = 8; // height of the lower Z flexure
z_flexures_z2 = min(sample_z - 12, 35); // " upper "
objective_mount_back_y = objective_mount_y + 2; //back of objective mount
z_anchor_y = objective_mount_back_y + z_strut_l + 2*zflex[1]; // fixed end of the flexure-hinged lever that actuates the Z axis
z_anchor_w = 20; //width of the Z anchor
zll = (z_strut_l + zflex[1])*z_lever_ratio; //required actuator lever length
zfz = z_flexures_z1; // shorthand for the next line only!
z_nut_y = z_anchor_y - zflex[1]/2 + sqrt(zll*zll - zfz*zfz);
z_actuator_travel = zll*0.15; // distance moved by the Z actuator
z_actuator_tilt = -asin(z_flexures_z1/zll); //angle of the Z actuator

z_flexure_x = (leg_r-zflex_l-max(5,leg[2]*0.1))*sqrt(2); // x position of the outside of the Z-axis static anchors (either side of the XY stage, on the X axis) (no longer used by Z axis but still in use elsewhere.)

bridge_dz = 10; // spacing between thin links on legs
base_t=1; // thickness of the flat base of the structure
wall_h=15; // height of the stiffening vertical(ish) walls
wall_t=2; //thickness of the stiffening walls
zawall_h = z_flexures_z2 - 10; //height of wall near Z anchor
zbwall_h = z_flexures_z2 - 10; //height of bridge over Z lever
illumination_clip_y = (-(leg_r-zflex_l-wall_t/2+leg_outer_w/2)/sqrt(2)
                       -wall_t/2-1); //position of clip for
                      // illumination/back foot.  This is set to
                      // coincide with the wall between the back
                      // two legs. TODO: remove this
illumination_arm_screws = [[20,z_nut_y,sample_z-2],[-20,z_nut_y,sample_z-2], 
                           [0,(leg_r + leg_outer_w)/sqrt(2) + 4,sample_z-2]];
                      // positions of screws that mount the adjustable version of the 
                      // illumination arm
condenser_clip_y = -8; //position of dovetail for old condenser assembly TODO: rename this
base_mounting_holes = [[-20,z_nut_y-4,0],
                       [20,z_nut_y-4,0],
                       [-z_flexure_x-4,big_stage?-8:-4,0],
                       [z_flexure_x+4,big_stage?-8:-4,0]]; 
                       // holes to screw the microscope to a baseplate

endstop_extra_ringheight=feet_endstops?1:0;
endstop_hole_offset=0;
//this is a temporary option to printfeet with smaller travel
//without this with 15mm hole the stage hits the objective
//the stage can move ~3mm in each direction, so the actuator only moves
//~1.7 mm
avoid_objective_xyfoot_offset=xy_actuator_travel-1.8;

fl_cube_w = 16; //width of the fluorescence filter cube

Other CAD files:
Minidrop build and test/Original files/version64_complete.dwg
Minidrop build and test/Original files/mDS_v12.dwg
Open Syringe Pump/Open Source Syringe Pump Library, PLOS ONE 2014/source files syringepump/linear_actuator_v0-2.stl
OpenFlexure Fluorescence Microscope/STL files/slide_riser_LS10.stl
OpenFlexure Fluorescence Microscope/design files/motor_driver_case.scad
Minidrop build and test/Original files/3d_printed_parts/mDS_base.stl
Minidrop build and test/Original files/3d_printed_parts/mDS_magshaft.stl
Minidrop build and test/Original files/3d_printed_parts/mDS_middle.stl
Minidrop build and test/Original files/3d_printed_parts/mDS_touchmount.stl
Open Syringe Pump/Open Source Syringe Pump Library, PLOS ONE 2014/source files syringepump/linear_actuator_v0-1.stl
Open Syringe Pump/Open Source Syringe Pump Library, PLOS ONE 2014/source files syringepump/linear_actuator_v0-3.stl
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

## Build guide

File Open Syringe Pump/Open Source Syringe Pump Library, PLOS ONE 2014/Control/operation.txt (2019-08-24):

Find attached the code for controlling the syringe pump. Also diagrams and wiring can be found here:

A4988 Stepper Motor Driver Module With Heat Sink #02258664
http://www.geeetech.com/wiki/index.php/StepStick_A4988_Stepper_Driver_Module

Arduino Uno
Instructions adapted from : http://howtomechatronics.com/tutorials/arduino/how-to-control-stepper-motor-with-a4988-driver-and-arduino/

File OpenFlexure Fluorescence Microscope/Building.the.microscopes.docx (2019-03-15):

This document is written by the Year 3 (2018/2019) Physics students from UCL (University College London) as a part of a Group Project.

Building the small (SS) microscope

These are the instructions that need to be followed to make the OpenFlexure 3D printed microscope after all the plastic parts were printed. The printing requires around 100 grams of plastic. The STL files that are required for 3D printing of all the parts are listed below. They can be found in the open source GitHub repository belonging to Richard Bowman [1]. It also contains all the details about the construction of the microscope and its structure.

Equipment list:

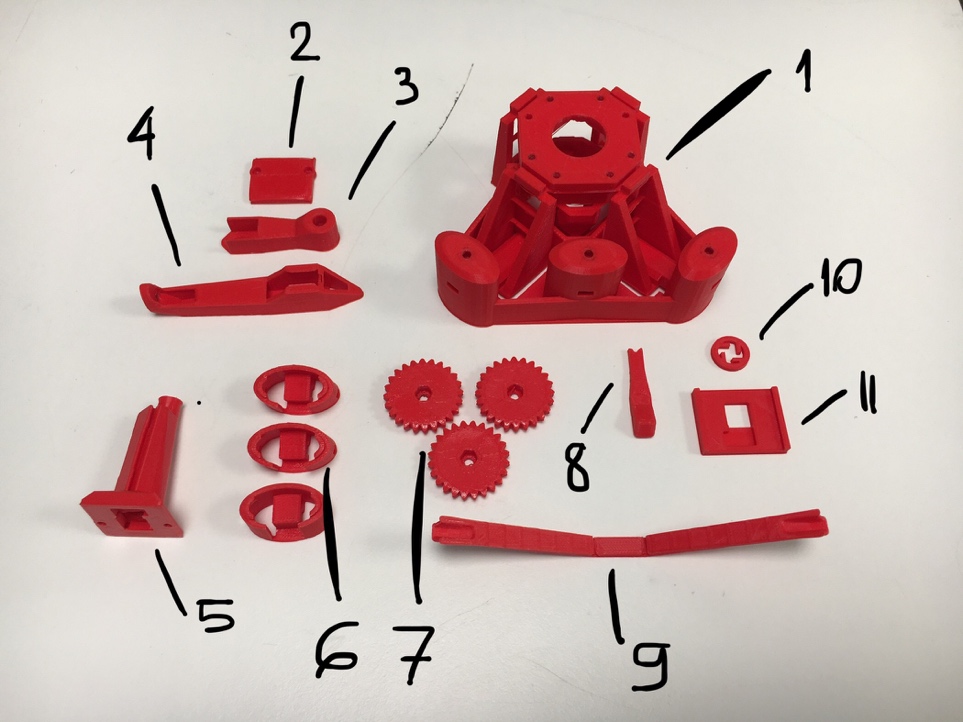
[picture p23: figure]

Figure 1. An image of all the 3D printed parts and tools needed to build SS OpenFlexure microscope. The names of all the pieces are listed below.

- 3D printed parts (figure 1):
  - Microscope body (1)
  - Optics module (5)
  - Illumination arm (3)
  - Rear foot (4)
  - Gears x3 (7)
  - Outer feet (tilted) x2 (6)
  - Middle foot (untilted) (6)
  - Raspberry Pi camera cover (2)
  - Sample holder clips x2
- 3D printed tools (figure 1):
  - Band tool (9)
  - Nut tool (8)
  - Camera board gripper (11)
  - Camera lens remover (10)

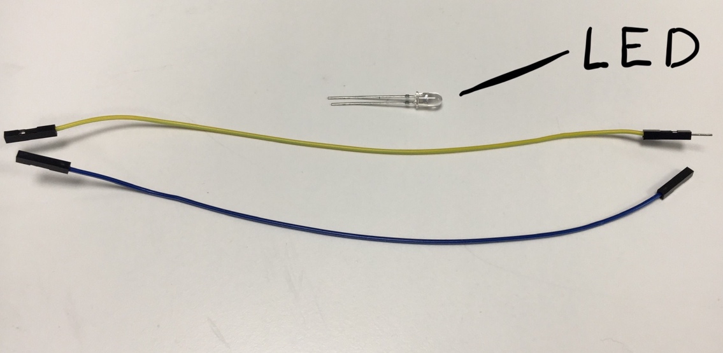
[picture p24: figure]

Figure 2. Some electronics needed to build the microscope. Shown: LED, jumping wires with male to female connectors (yellow) and female to female connectors (blue).

- Electronics (figure 2):
  - Jumping wires with female to female x3
  - Jumping wire with female to male x1
  - LED (white) x1
  - Resistor (330 Ohm)
  - Raspberry Pi computer control unit (and all the associated devices) x1
  - Raspberry Pi version 2 camera module (with lens) x1
- Hardware:
  - M3 screws (25 mm) x3
  - M3 screws (8 mm) x4
  - M2 screws (8 mm) x2
  - M3 nuts x6
  - M2 washers x2
  - M3 washers x3
  - Small elastic bands x3
- Tools:
  - Hex key
  - Screwdriver
  - Craft knife

Names of the STL files:

- 3D printed parts:
  - body_SS.stl
  - optics_picam2_pilens.stl
  - illumination_and_back_foot_adj_SS.stl
  - gears.stl
  - sample_clips.stl
  - feet.stl
  - picamera_2_cover.stl
- 3D printed tools:
  - actuator_assembly_tools.stl
  - picam2_lens_remover.stl
  - picam2_board_gripper.stl

Method:

1. Obtain the 3D printed parts and tools. The low-quality mode (0.15 mm layers) should be used to make sure any bridges, that appear during the print, are stable. If Ultimaker 2+ 3D printer is used – all the parts can fit on the printer bed without overlapping, so just one print is sufficient (figure 3). No support material is needed for the printing.

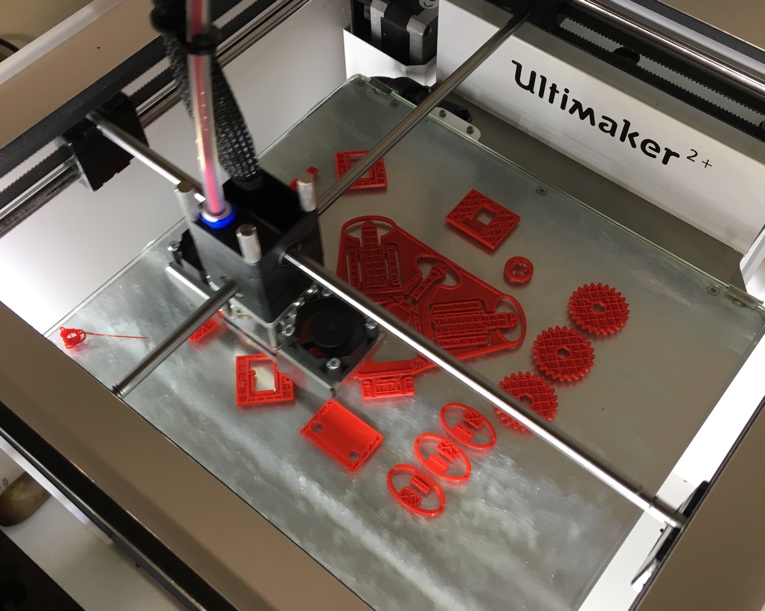
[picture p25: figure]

Figure 3. The first few layers printed on the bed of the Ultimaker 2+ 3D printer.

2. Using the band tool snap all the supports that were printed. There are 2 supports in each actuator column and 2 supports linking the mount for the optics module to the microscope body frame.
3. Cut all the loose pieces of plastic which resulted during the printing using the craft knife.
4. Assemble the gears with the elastic bands:
  4.1. Put the M3 nuts inside the hexagonal holes in the gears (figure 4). Screw the 25 mm M3 screws in the nuts.

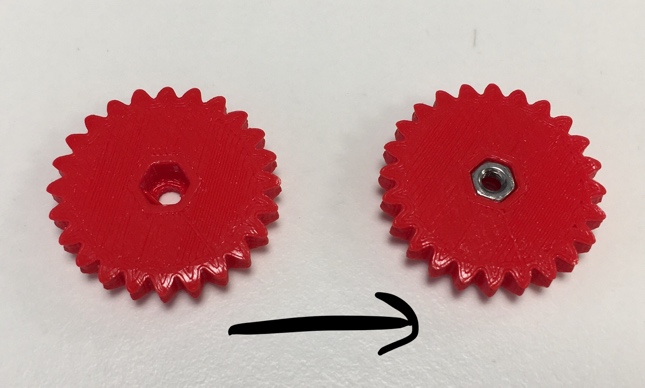
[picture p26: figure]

Figure 4. Transition from the freshly printed gear to the gear in which a screw can be screwed in.

  4.2. Put another set of the M3 nuts through the holes on the sides of the actuator columns. Each nut should be inserted corner-first to prevent it from jamming.
  4.3. Place the washers around the holes on top of the actuator columns. Insert the screws through the gears, washers and holes (on top of the actuator columns). Screw them in loosely into the nuts that are inside the actuators. Use the nut tool to hold the nuts tight in place one by one while doing this. This is shown in detail in figure 5.

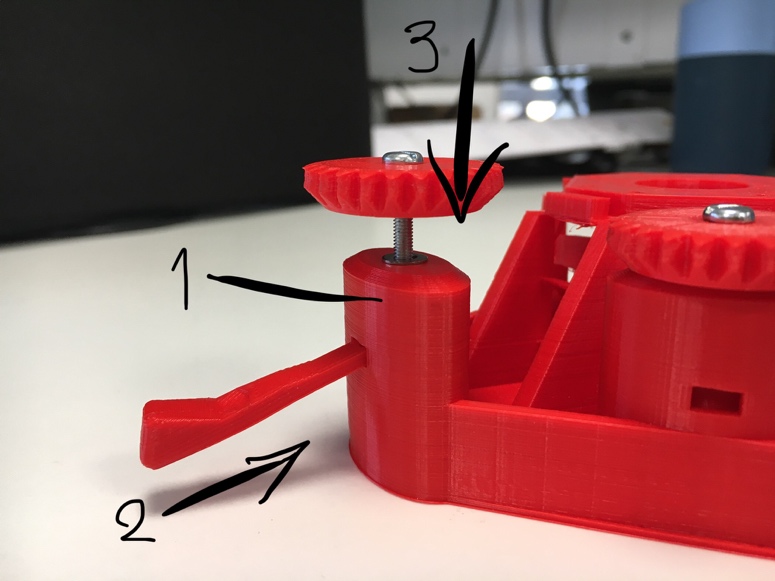
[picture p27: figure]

Figure 5. 1 – actuator column, 2 – nut tool holding a nut in place, 3 – screw in.

  4.4. Fit the outer and middle feet to the bottom of the microscope. Hook the elastic bands over the ends of the band tool and put them through the microscope feet one by one. The band should grab the hooks and click inside the actuator column. The band pulls the actuator down and the gear should feel more resistance when it is turned. This part is vital for focus control and navigation through a slide with a sample on it (by turning the gears).
  4.5. The middle part of the bands should hold the feet of the microscope in place (figure 6). Make sure all 3 actuators are done correctly.

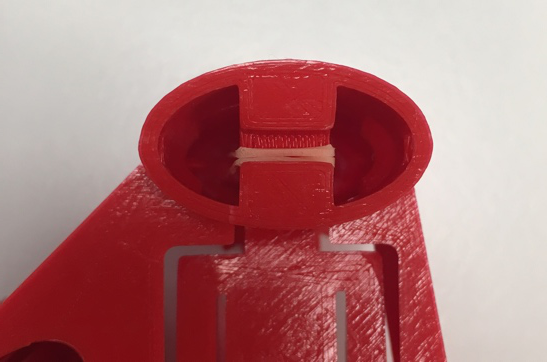
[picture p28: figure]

Figure 6. The orange band (under tension) is holding the foot in place.

5. Assemble the illumination module:
  5.1. Take the rear foot and thread the jumping wires with female to female connectors through the opening in the foot.
  5.2. Screw the horizontal illumination arm to the vertical rear foot using the M3 8mm screw, the nut and the washer (figure 7). Put the end of the jumping wire through the opening in this part.

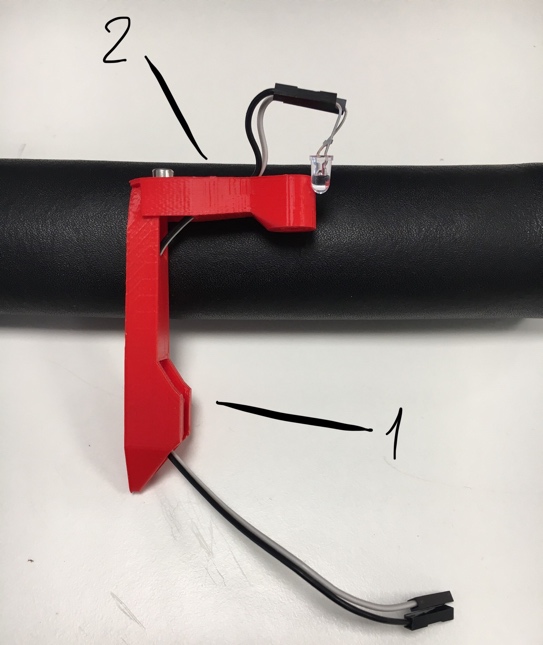
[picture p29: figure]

Figure 7. Illumination module: 1 – rear foot, 2 – illumination arm.

  5.3. Connect the LED to the jumping wires and fit it into the light bulb opening in the horizonal illumination arm.
  5.4. Connect the 330 Ohm resistor to one of the wires sticking from the bottom of the illumination arm. Connect another female to female jumping wire to the other end of the resistor and a male to female wire to the unused connector of the second wire.
  5.5. Connect both of the wires to the Raspberry Pi control unit.
  5.6. Slide on the illumination module on to the dovetail mount at the back of the microscope body (figure 8). Make sure it is slid from the bottom.

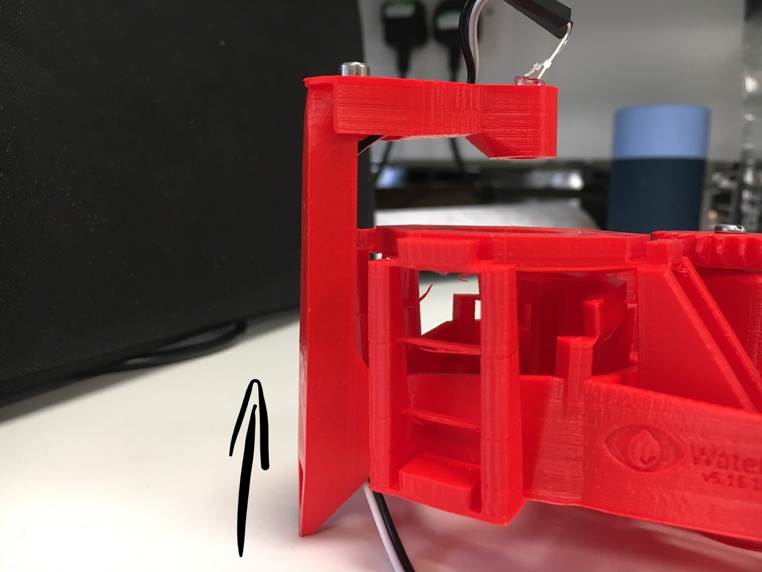
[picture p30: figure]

Figure 8. Sliding the illumination module into the microscope body from the bottom.

6. Integrate the Raspberry Pi camera module with the optics module. This has to be done carefully as the camera sensor is very sensitive and the lens is very fragile:
  6.1. Remove the protective film from the camera lens.
  6.2. Fit the lens on the camera module through the opening in the camera board gripper so the camera module is static.
  6.3. Put the camera lens remover over the lens. The hooks on the remover should be pointing anti-clockwise. Turn the remover to unscrew the lens making sure that the board gripper is holding the camera module in place.
  6.4. Carefully take the lens that has just been removed and fit it on top of the optics module (figure 9). This requires a bit of force. Make sure the lens is the same way up as it was on the camera module.

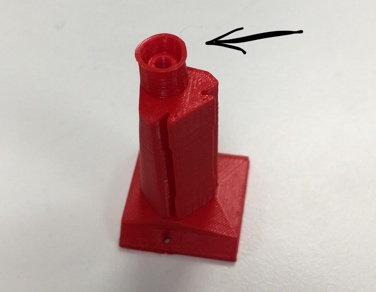
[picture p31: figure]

Figure 9. The lens from the Raspberry Pi camera module must be fit in the opening.

  6.5. Put the rest of the camera module under the optics module making sure that it fits in the hole which is designed specifically for this camera model. Put the camera cover over it and screw the 8 mm M2 screws in to hold it tight in place. The detailed overview can be found in figure 10.

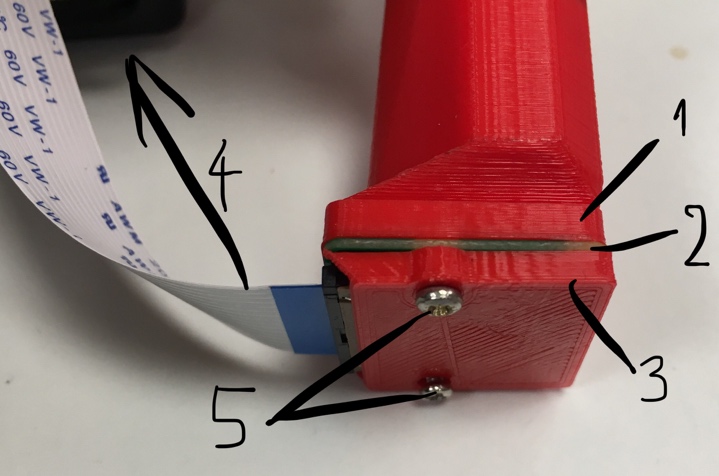
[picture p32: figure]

Figure 10. Integration of the Raspberry Pi camera module with the optics module. 1 – optics module, 2 – camera module, 3 – camera cover, 4 – to the Raspberry Pi control unit, 5 – M2 screws.

  6.6. Slide the optics module in the opening in the microscope body onto the dovetail mount (figure 11) and connect the camera module to the Raspberry Pi control unit.

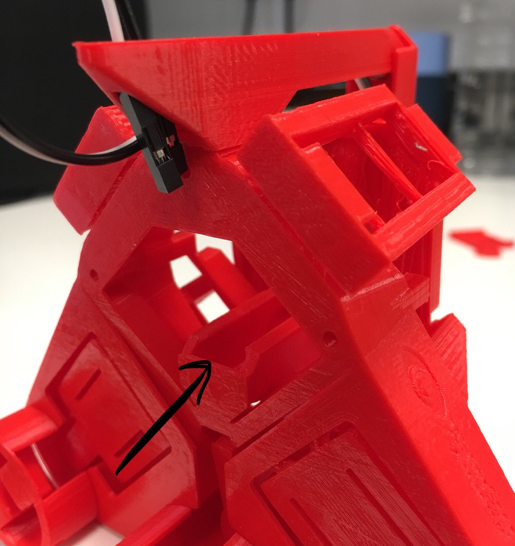
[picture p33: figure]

Figure 11. Dovetail mount in the microscope body for the optics module.

7. Screw the sample holder clips in the holes on the top of the microscope body using 8mm M3 screws.

Building the larger (LS65) microscope

To make the larger (LS65) microscope, the same instructions need to be followed with some minor changes and additions. Moreover, another set of the 3D printed parts are needed (described later). Most of the 3D printed parts are different than the ones for the smaller microscope. The parts are bigger and thus are taking longer to print. As before, all the details about the structure and the parts can be found in the Richard Bowman’s GitHub repository [1]. Figure 12 shows both SS and LS65 microscopes standing side by side.

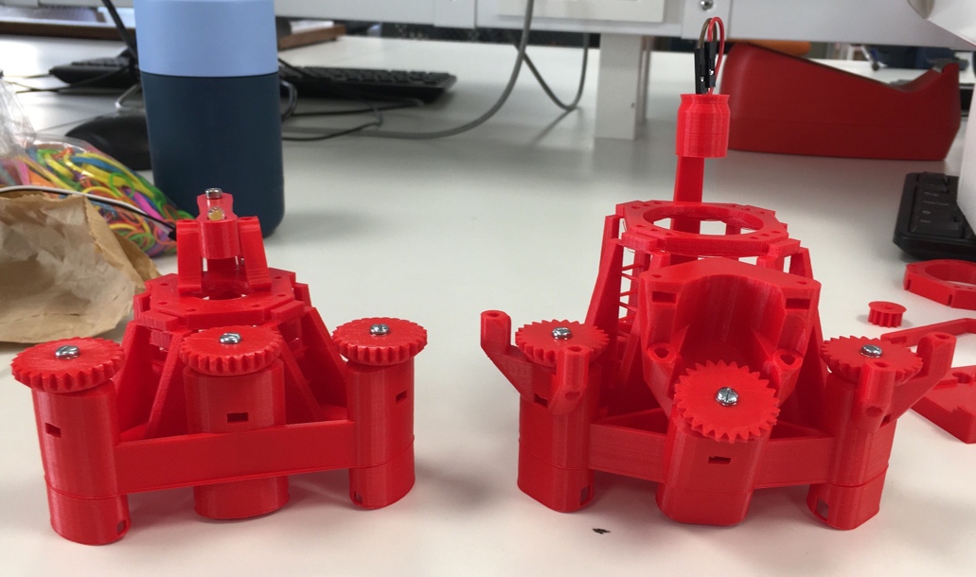
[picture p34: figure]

Figure 12. Smaller SS (left) and larger LS65 (right) OpenFlexure microscopes. The LS65 microscope is missing sample clips (used in the SS microscope).

Extra equipment list:

- Illumination head (figure 13)
- M3 screw (8mm) x1
- M3 head x1

Names of the STL files:

- 3D printed parts:
  - main_body_LS65-M.stl
  - optics_picamera_2_pilens_LS65.stl
  - illumination_and_rear_foot_LS75.stl
  - gears.stl
  - small_gears.stl
  - sample_clips.stl
  - feet.stl
  - picamera_2_cover.stl
- 3D printed tools:
  - actuator_assembly_tools.stl
  - picam2_lens_remover.stl
  - picam2_board_gripper.stl

Changes in the method:

- Step 5 (assembling the illumination module):
  - Illumination head should be slid on to the dovetail mount on the illumination arm.

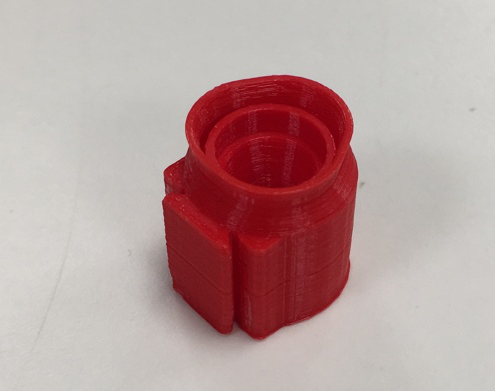
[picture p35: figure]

Figure 13. Illumination head.

  - The LED is then placed in the head.
- Step 6 (optics module):
  - The optics module for the larger microscope looks a bit different comparing to the smaller one.
  - The M3 nut is placed in the small pocket on the side of the optics module (figure 14 (1)).
  - The 8mm M3 screw is then screwed in this nut through the hole that was specifically designed for this (figure 14 (2)).

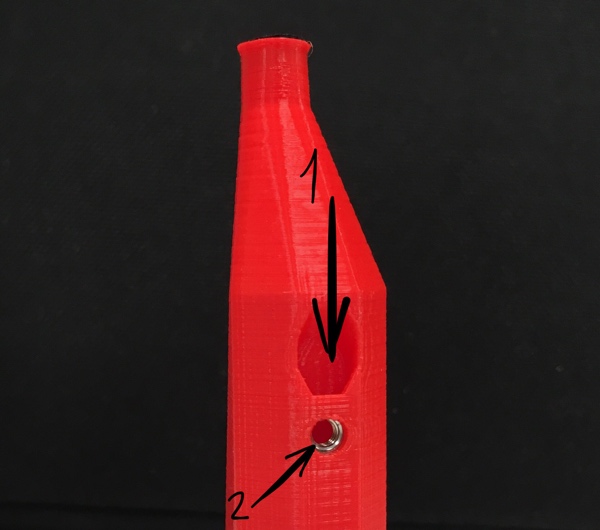
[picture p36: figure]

Figure 14. The top of the LS65 optics module. 1 – a pocket for M3 nut, 2 – a hole for M3 screw.

  - When the optics module is integrated with the main body of the microscope, the screw is placed into the internal slit on the inside of the body. This is done going from the bottom upwards.

References

[1] https://github.com/rwb27/openflexure_microscope

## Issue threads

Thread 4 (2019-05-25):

### ISSUE TITLE
Some links lead to 404s..

### ISSUE THREAD

**Issue by amchagas** [MakerTobey/OpenMicrofluidics#4]
Hi!

This is super interesting!
Some links are leading to 404/403 errors though:

https://github.com/MakerTobey/OpenMicrofluidics/tree/master/Open%20FADS

https://github.com/MakerTobey/OpenMicrofluidics/tree/master/pressure%20control%20bild%20and%20test

https://media.proquest.com/media/pq/classic/doc/4322030507/fmt/ai/rep/NPDF?_s=EUAbzVz%2B%2FEKGyiix9oguFSmtgAU%3D

**Comment by MakerTobey** [comment]
Thanks a lot! now fixed.

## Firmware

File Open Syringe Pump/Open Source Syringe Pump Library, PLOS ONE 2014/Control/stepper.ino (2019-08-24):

/*     Simple Stepper Motor Control Exaple Code
 *  adapted from:   
 *  by Dejan Nedelkovski, www.HowToMechatronics.com
 *  
 */
// defines pins numbers

const int stepPin = 3; 
const int dirPin = 4; 
const int stepPin2 = 6; 
const int dirPin2 = 5; 

void setup() {
  // Sets the two pins as Outputs
  pinMode(stepPin,OUTPUT); 
  pinMode(stepPin2,OUTPUT); 
  pinMode(dirPin,OUTPUT);
  pinMode(dirPin2,OUTPUT);

}

void loop() {
  digitalWrite(dirPin,LOW); // Enables the motor to move in a particular direction
  digitalWrite(dirPin2,LOW); // Enables the motor to move in a particular direction
  // Makes 200 pulses for making one full cycle rotation
  for(int x = 0; x < 200; x++) {
    digitalWrite(stepPin,HIGH); 
    digitalWrite(stepPin2,HIGH); 

    delayMicroseconds(1000); 
    digitalWrite(stepPin,LOW); 
    digitalWrite(stepPin2,LOW); 

    delayMicroseconds(1000); 
  }
  delay(1000); // One second delay
  
//  digitalWrite(dirPin,LOW); //Changes the rotations direction
  // Makes 400 pulses for making two full cycle rotation
//  for(int x = 0; x < 400; x++) {
//    digitalWrite(stepPin,HIGH);
//    delayMicroseconds(1000);
//    digitalWrite(stepPin,LOW);
//    delayMicroseconds(1000);
//  }
//  delay(1000);
}

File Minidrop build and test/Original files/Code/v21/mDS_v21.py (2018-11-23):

#!/usr/bin/env python3

#==============================================================
#
# Shell program Authors:      Christine Smythe and Colin Smythe (Dunelm Services Limited)
#
# Author:       William Stephenson
# Version/Date: v21 8/2/2017
# Notes:        Heavily modified for miniDrops system      
#
# Description:  This simple Python3 program is used to take a single photo,
#               or a video with the RPi-Camera. 
#               This program requires Python3.
#
#               For a single photo the user needs to enter a filename eg myphoto
#               to which the program will add .jpg
#               The file will be created in the users current directory -
#               so make sure you are in the right current working
#               directory before running the program.
#               If you chose a filename already in use the contents will be
#               overwritten by the new photo
#
#               For a video the user needs to specify a filename eg myvideo to which
#               the program will add .h264
#               then press 'Start video' to start recording and
#               'Stop video' to stop recording.
#
#               Please ensure you press 'QUIT' rather than closing the window in order to 
#               cleanly close the camera preview window.
#
#               If you want to view any of the images then simply use the file manager and
#               double click on the filename. This doesn't work for videos.
#
#               The program also contains buttons for opening/closing a set of solenoids. 
#               This is a single signal (GPIO pin = 18, BCM numbering) either HIGH or LOW
#
#               Additionally the program runs background control of stepper motor rotaiton. 
#               Parameters for no. of steps, speed, and wait time can be found in the worker 
#               function at the bottom of the program.
#
#               Pressures are read through an SPI interface in ADC and require spidev package.
#
#               MicroAir pump is controlled through "PUMP ON/OFF" buttons.
#
# History:      Original release.
#
# Copyright:    2013 (c) Premier Farnell Limited
#
# License:      GPLv3+
#
#==============================================================

import tkinter as tk
from tkinter import *
from time import sleep
import picamera
import os
import sys
import RPi.GPIO as GPIO
import spidev
import threading
import multiprocessing
import logging

#######################################################
# Honeywell Pressure sensor calibration parameters 
m = 55.596 # slope [bits/PSI]
b = 102.4  # intercept [bits]
#######################################################


#######################################################
# Setup GPIO pin(s)
GPIO.setmode(GPIO.BCM)
GPIO.setwarnings(False)

DIR_PIN = 19    # Stepper motor Direction PIN
STEP_PIN = 20   # Stepper motor Step PIN

sol1_pin = 22    # Solenoid 1 PIN
sol2_pin = 23    # Solenoid 2 PIN

pump_pin = 27


GPIO.setup(sol1_pin, GPIO.OUT)        
GPIO.output(sol1_pin, False)          

GPIO.setup(sol2_pin, GPIO.OUT)
GPIO.output(sol2_pin, False)

GPIO.setup(pump_pin, GPIO.OUT)
GPIO.output(pump_pin, False)

GPIO.setup(DIR_PIN, GPIO.OUT)
GPIO.setup(STEP_PIN, GPIO.OUT)
#######################################################


#######################################################
# Setup SPI protocol for Analog-to-Digital Converter
spi = spidev.SpiDev()
spi.open(0,0)
#######################################################

#==============================================================
# Declaration of Constants
# none used

#==============================================================


class Application(Frame):
    """ GUI Application for taking photos. """
    def __init__(self, master):
        super(Application, self).__init__(master)
        self.grid()
        self.create_widgets()
        self.setup_camera()
        self.poll()
        
    #.................Method: create widgets..........................
    # This creates a window with buttons 
    #   - to take a single photo or a video.
    #   SA single photo just needs the user to enter a filename to put
    #   the photo in. The filename is appended with .jpg and the file
    #   placed in the users current directory.
    # 
    #   A video needs a filename to store the video in adn again will be
    #   created in the users current directory.
    #

    
    def create_widgets(self):
        """ Create widgets for photos. """

        #setup widgets to get filename for single photo
        Label(self, text = "Image Filename:").grid(row = 0, column = 0, sticky = N+S)
        self.s_filename = Entry(self)
        self.s_filename.grid(row = 1, column = 0)

        # create 'Take Image' button
        Button( self,
                text = "Take Image",
                command = self.action_camera,
                bg='white',
                ).grid(row=2, column = 0, sticky = N+S)

        
        #setup widgets to get filename for video
        Label(self, text = "Video Filename :").grid(row = 0, column = 1, sticky = N+S)
        self.v_filename = Entry(self)
        self.v_filename.grid(row = 1, column = 1)

        Label(self, text = 'Oil Pressure:').grid(row = 6, column = 0, sticky = E)
        Label(self, textvariable = press1).grid(row = 6, column = 1, sticky = W)
        Label(self, text = 'Aq. Pressure:').grid(row = 5 , column = 0, sticky = E)
        Label(self, textvariable = press2).grid(row = 5, column = 1, sticky = W)

        # create 'RUN' Button
        Button( self,
                text = "RUN",
                command = self.open_solenoids,
                bg='green',
                ).grid(row=8, column = 0, sticky = E+N+S)


        # CREATE 'STOP' Button
        Button( self,
                text = "STOP",
                command = self.close_solenoids,
                bg='red',
                ).grid(row=8, column = 1, sticky = W+N+S)

        # create 'Start Video' button
        Button( self,
                text = "Start video",
                command = self.start_video,
                bg='green',
                ).grid(row=2, column = 1, sticky = N+S)

        # create 'Stop video' button
        Button( self,
                text = "Stop Video",
                command = self.stop_video,
                bg='green',
                ).grid(row=3, column = 1, sticky = N+S)

        # create 'PUMP-ON' button
        Button( self,
                text = "PUMP ON",
                command = self.pump_on,
                bg='green',
                ).grid(row=7, column = 0, sticky = W+E+N+S)

        # create 'PUMP-OFF' button
        Button( self,
                text = "PUMP OFF",
                command = self.pump_off,
                bg='red',
                ).grid(row=7, column = 1, sticky = W+E+N+S)

        # create 'QUIT' button
        Button( self,
                text = "QUIT",
                command = self.exit_camera,
                bg='red',
                ).grid(row=9, column = 1, sticky = W+E+N+S)

        # create text field to display results
        self.results_txt = Text(self, height = 2, wrap = WORD)
        self.results_txt.grid(row = 10, column = 0, columnspan=2)
        
        
    def poll(self):
        self.master.after(250, self.poll)

    #.................... Method: choose_single_photo ................
    # This method selects the single photo option
    # and asks the user to enter a filename and press ACTION 
    #
    def choose_single_photo(self):
        self.chosenfile = StringVar()
        self.chosenfile.set(None)
        status = ""
        status = "You have chosen to take a single photo.\n"
        status = "Make sure you have entered a filename then\n"
        status += "press 'Execute' when ready\n" 
        self.results_txt.delete(0.0, END)
        self.results_txt.insert(0.0, status)        
 
    # ................. end of method choose_single_photo .................

    #.................... Method: action_camera ................
    # This method calls appropriate method depending on which
    # photo option user has chosen
    #
    def action_camera(self):
        status = ""
        self.action_single()
    

    # ................. end of method action camera .................

    
    
    #.................... Method: action_single ................
    # This method takes a single photo
    # and updates the status display to show the name of the file it is saved in
    #
    def action_single(self):
        status = ""
        numphotos = 1
        numsecs = 1
        chosenfile = ""

        #first get filename
        contents= self.s_filename.get()
        #convert to string and add .jpg
        self.chosenfile= str(contents)+ ".jpg"
        status = "\nchosen filename : " + self.chosenfile + "     "

        #now take photo
        try:
            self.camera.capture(self.chosenfile)
            status += "captured image - " + self.chosenfile
        except:
           status += "Invalid file namechosen - " + self.chosenfile

        self.results_txt.delete(5.0, END)
        self.results_txt.insert(5.0, status)

    # ................. end of action_single .................
    
    
    #.................... Method: start_video ................
    # This method gets the filename the user has entered, starts the video
    # and updates the status display to show the name of the file it is saved in
    #
    def start_video(self):
        status = ""
        chosenfile = ""

        #first get filename
        contents= self.v_filename.get()
        #convert to string and add .h264 for file format
        self.chosenfile= str(contents) + ".h264"
        status = "chosen filename : " + self.chosenfile + "\n"
 
        # now start the recording
        try:
            status += "\nStarting to record   \n"
            self.camera.start_recording(self.chosenfile)
        except:
            status += "Invalid file name chosen - " + self.chosenfile + "\n"          

        self.results_txt.delete(0.0, END)
        self.results_txt.insert(0.0, status)

    # ................. end of start_video .................
    

    #.................... Method: stop_video ................
    # This method stops the video recording
    # and updates the status display 
    #
    def stop_video(self):
        status = ""
        chosenfile = ""
        try:
            self.camera.stop_recording()
            status += "stopped recording \n " 
        except:
            status += "Error on stop recording \n"     

        self.results_txt.delete(6.0, END)
        self.results_txt.insert(6.0, status)

    # ................. end of stop_video .................
    
      
    #.................... Method: exit_camera ................
    # This method closes down the camera nicely and exits
    #
    def exit_camera(self):
        status = ""
        useranswer = ""
        useranswer = "no"
        cancelquestion = "You are still recording a video.\nDo you wish to stop recording ?"
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

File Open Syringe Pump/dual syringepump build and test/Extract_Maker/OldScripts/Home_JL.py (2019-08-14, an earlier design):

import piplates.MOTORplate as MOTOR
import RPi.GPIO as GPIO
import time
import os
import string
from Tkinter import *
import tkFont

print MOTOR.getID(0)

#flush out any old interrupts
#dummy = MOTOR.getINTflag0(1)
#intFLAG=0
#intITS=0

#def moveDone(channel):
#    global intBITS, intFLAG
#    intBITS=MOTOR.getINTflag0(0)
#    intFLAG=1

MOTOR.RESET(0)

#configure steppers A and B for homing function
MOTOR.stepperCONFIG(0,'a','ccw','M8',100,0)
MOTOR.stepperCONFIG(0,'b','ccw','M8',100,0)



#move steppers A and B towards switches
MOTOR.stepperJOG(0,'a')
MOTOR.stepperJOG(0,'b')

#GPIO.setmode(GPIO.BCM)
#GPIO.setup(22, GPIO.IN, pull_up_down=GPIO.PUD_UP)
#GPIO.add_event_detect(22, GPIO.FALLING, callback=moveDone)
#allow interrupts when a motor stops
#MOTOR.enablestepSTOPint(0,'a')
#MOTOR.enablestepSTOPint(0,'b')
#MOTOR.intEnable(0)


flag=1
motorA=1
motorB=1


while(flag):
    time.sleep(0.1)
    stat=MOTOR.getSENSORS(0)
    if not (stat&0x01):
        MOTOR.stepperSTOP(0,'a')
        time.sleep(0.1)
        MOTOR.stepperCONFIG(0,'a','cw','M8',100,0)
        MOTOR.stepperMOVE(0,'a',50)
        MOTOR.stepperOFF(0,'a')
        motorA=0
        print "MOTOR A stopped"
    if not (stat&0x04):
        MOTOR.stepperSTOP(0,'b')
        MOTOR.stepperCONFIG(0,'b','cw','M8',100,0)
        MOTOR.stepperMOVE(0,'b',50)
        MOTOR.stepperOFF(0,'b')
        motorB=0
        print "MOTOR B stopped"
    if (motorA==0 and motorB==0):
        flag = 0
        print"End Stop Reached"
        

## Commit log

2018-11-23 populate repository
    [BOM.xlsx, Mouser_Nov_23_2018.xlsx, mDS_base.stl, mDS_lensmount.stl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]
2019-01-10 BOM information updated
    [BOM.xlsx, from hackaday download mDS_BOM_v1.xlsx]
2019-01-17 update to BOM and purchases
    [BOM.xlsx]
2019-01-30 extension and new projects
    [BOM dual syringe pump.xlsx, BOM.xlsx, Jameco cart - where to buy in Europe?.csv, Mouser_Nov_23_2018.xlsx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]
2019-02-01 order updates
    [USA_purchase_overview.xlsx, USA_purchase_overview_January19_public.xlsx]
2019-03-12 added material LEDs and filters
2019-03-14 update optical filters and power supply considerations
2019-03-15 added open flecturescope
    [1_inch_disc_holder.scad, 1_inch_disc_holder.stl, RMS_tube_picamera.stl, actuator_assembly_tools.scad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]
2019-03-15 names changed
    [BOM dual syringe pump.xlsx, fl_cube.stl, fl_cube_outer.stl]
2019-03-15 further name changes
    [1_inch_disc_holder.scad, 1_inch_disc_holder.stl, RMS_tube_picamera.stl, actuator_assembly_tools.scad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]
2019-03-15 sorted print files
    [picamera_2_cover.stl]
2019-04-24 updates and selection
    [BOM.xlsx, actuator_assembly_tools.stl, back_foot.stl, condenser.stl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]
2019-04-25 BOM updated
    further components ordered
    [BOM.xlsx]
2019-07-24 update of folders and syringe pump
    [BOM dual syringe pump.xlsx, BOM.xlsx, Syringe Pump and gears.3mf, Syringe_pump_PI_holder.3mf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]
2019-08-07 printing progress
    [Syringe Pump and gears.3mf, Syringe_pump_PI_holder.3mf, extractmaker_holder_v4.STL, motor_base_v10.STL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]
2019-08-14 addintional files syringepump
    [BOM dual syringe pump.xlsx, SupplementalFile-S1-HeatSink_V2.STL]
2019-08-14 photo added
    [flexurescope_high_res_opics_motors_ultimaker3.3mf]
2019-08-20 new material
    [OpenAPD_BOM.ods]
2019-08-24 add subprojects and files as well as build photos
    [BOM.xlsx, SupplementalFile-S1-HeatSink_V2.STL, linear_actuator_v0-1 (1).amf, linear_actuator_v0-1.stl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]
2020-03-09 Update README.md
    Updates added on current work and repositories of emphasis.
2020-03-17 update fluorescence filters available
2020-03-17 update filter spec sheets
2020-03-19 move folders to right place
    [1_inch_disc_holder.scad, 1_inch_disc_holder.stl, BOM dual syringe pump.xlsx, RMS_tube_picamera.stl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]
2020-03-19 correct sub-repository name
    [uCube.stl, uFace.stl]
2020-03-24 upload microscope design
    [openscad_reflection_illuminator_FL_LED_star_2_screws_curved_2_wide.scad, openscad_reflection_illuminator_FL_LED_star_2_screws_curved_2_wide.stl]
2020-03-25 upload parts
    [actuator_assembly_tools.scad, back_foot.scad, camera_platform.scad, endstop.scad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]
2020-06-18 add recent publication on voltage booster
2020-08-05 updated files fluorescence microscope
    [actuator_assembly_tools.stl, condenser.stl, feet.stl, fl_cube.stl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]
2023-02-06 update with thread design
2025-12-08 Update BOM dual syringe pump.xlsx
    [BOM dual syringe pump.xlsx]
